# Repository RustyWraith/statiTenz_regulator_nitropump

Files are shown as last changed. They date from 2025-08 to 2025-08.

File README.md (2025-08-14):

# statiTenz_regulator_nitropump

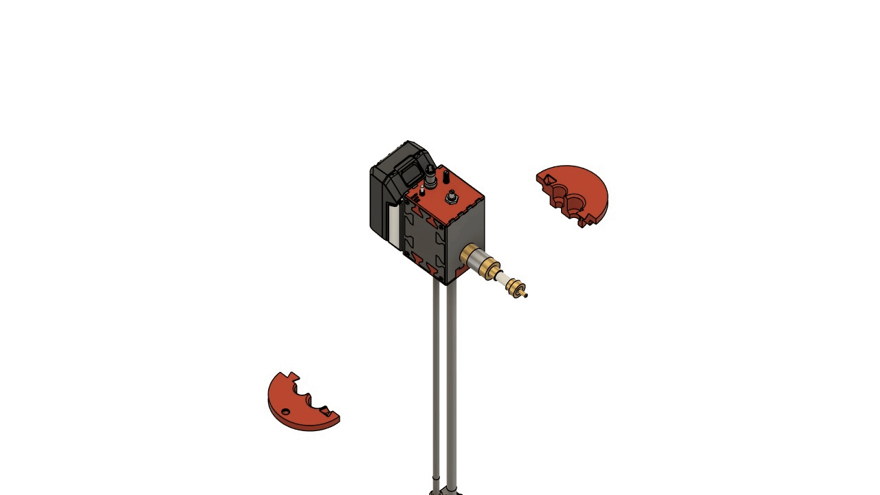
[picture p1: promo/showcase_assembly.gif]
showcase_assembly
  

Designed as part of the [**_statiTenz project_**](https://github.com/topics/statitenz).

## Application

Designed to pump liquid nitrogen from one vessel to another.

## Operating principle

Brushless DC motor actuated impeller pushes liquid nitrogen up the pipe.

## Basic operations

- Switch in **OFF** position
  The device remains powered off.
- Switch in **AUTO** position
  The motor speed is controlled by the PWM pin in the 3-pin connector.
- Switch in **ON** position
  The motor speed is manually controlled using the large knob, while the small knob sets the maximum speed limit.

## Operation tips

📝 Ensure the device is fully cooled before operation.  
📝 The check valve prevents ice formation inside the top part of the device.  
⚠️ **Do not** seal any vessel containing liquid nitrogen.  
⚠️ Exposing the cooled pumping part to the atmosphere will quickly cause ice to form inside the motor. Defrost and dry it at room temperature.  
⚠️ Plastic parts may explode upon cooling or heating. Let them settle at least 10 minutes before handling.  

## Assembly tips

Click on CODE -> Download ZIP to download all project files.  
Assemble the device following the instructions in the CAD_files\drawings folder.  
Refer to the schematics_and_PCBs folder for wiring instructions.  
The bill of materials is available in the CAD_files\buying_BOMs folder.  
Replace the motor's bearings with ceramic ones to ensure proper operation in liquid nitrogen.  
Handle ceramic bearings carefully, as they are fragile. It is recommended to purchase a spare set.  
Use the printed jigs (bearing_removing_jig_1 and bearing_removing_jig_2) to remove the stock bearings.  
PTFE sealing tape works fine.  
PTFE is generally a suitable material for use with liquid nitrogen.  
Print all parts in PETG. While PET performs adequately in liquid nitrogen, it may experience fatigue over time.  

statiTenz_regulator_nitropump_head  

statiTenz_regulator_nitropump_pump  

## Demo

Watch a short demonstraition [here](https://youtu.be/WFPVAQTfw5o) and [here](https://youtu.be/W20JA836Wec).  
Or [here](https://rutube.ru/video/cd4911075f1441f6e3c4c198d58dbadf) and [here](https://rutube.ru/video/834853d1d1c72582e7ad7376b3be9698).  

## Contact the author

Create a new issue.  

## Donate the author

[donate][boosty-link]  

[boosty-link]: https://boosty.to/rustywraith/donate
[boosty-image]: promo/boosty.png

[][cc-by]  
[][cc-by]  

[cc-by]: http://creativecommons.org/licenses/by/4.0/
[cc-by-image]: https://i.creativecommons.org/l/by/4.0/88x31.png
[cc-by-shield]: https://img.shields.io/badge/License-CC%20BY%204.0-lightgrey.svg

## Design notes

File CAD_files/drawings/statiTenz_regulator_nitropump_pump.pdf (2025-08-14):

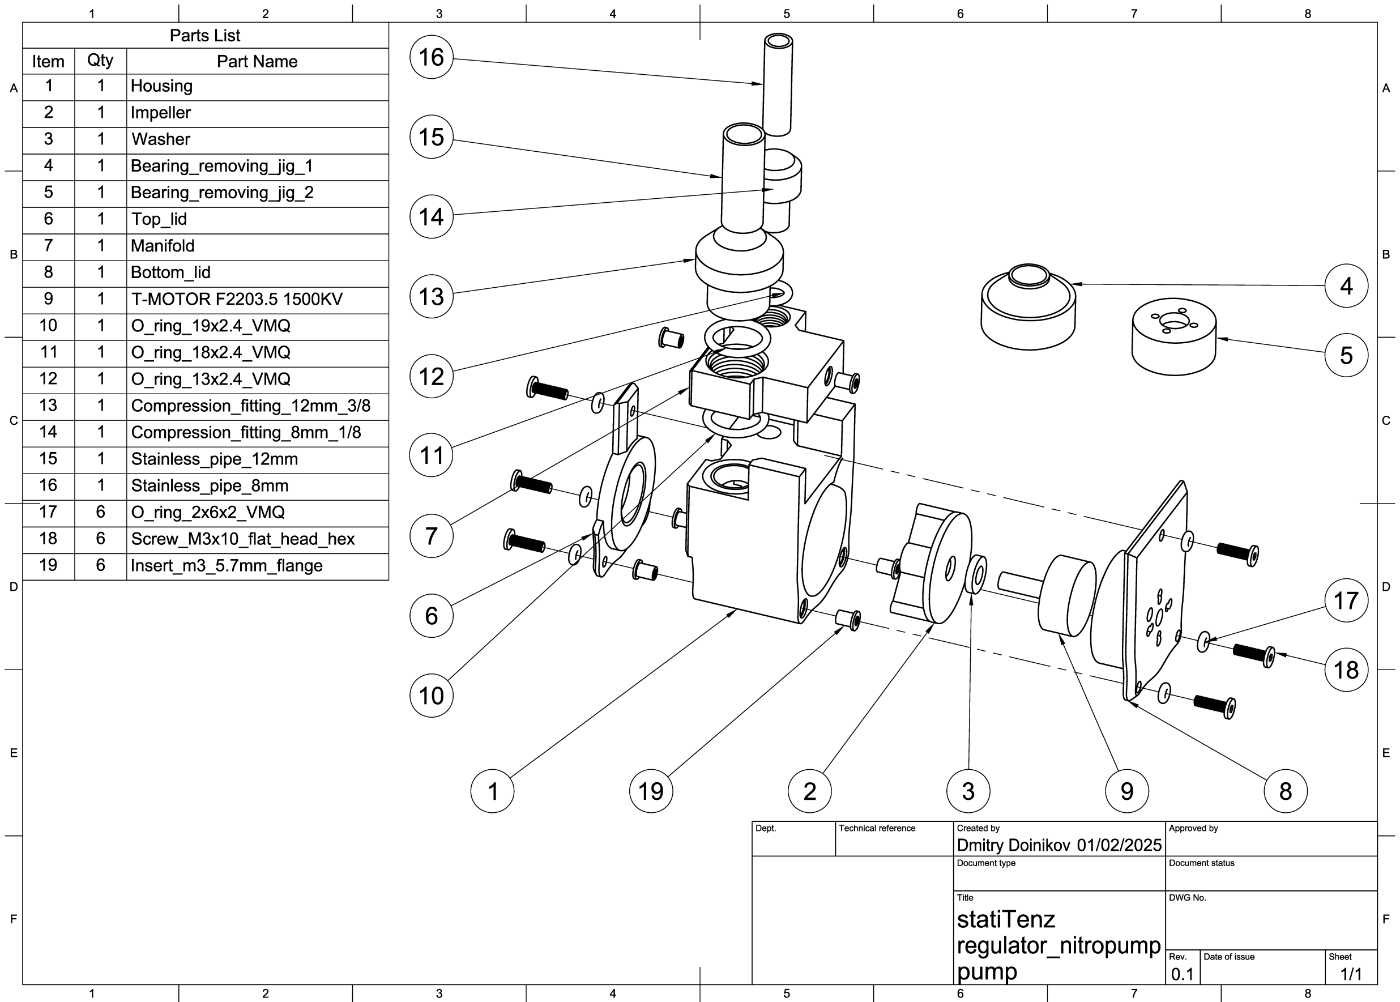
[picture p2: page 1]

1 | 2 | 3 | 4 | 5 | 6 | 7 | 8
Parts List
Item Qty | Part Name
Al | 1 | 1 | Housing | I | --i | I | IA
2 | 1 | Impeller
3 | 1 | Washer
4 | 1 | Bearing_removingjig_ 1
5 | 1 | Bearing_removingjig_ 2
6 | 1 | Top_lid
_----+-. - A | 1B -
7 | 1 | Manifold | I | - Bl I | 8 | 1 | Bottom_lid
9 | 1 | T-MOTOR F2203.5 1500KV
'-..____/
10 | 1 | O_ring_ 19x2.4_VMQ | l~J C o~o
11 | 1 | O_ring_ 18x2.4_VMQ
12 | 1 | O_ring_ 13x2.4_VMQ
Compression_fitting_ 12mm_3/8 1 | IC
13 | 1
c: | ~ | 1 IR -------l '-- ~ i:=::::::n-v---r I Compression_fitting_8mm_ 1/8 | I 14 | 1
15 | 1 | Stainless pipe_ 12mm

# ~(!Jr~~/ -- I

'-...._____/
------ ¹⁶ 1 I Stainless_pipe_8mm | r--.._
------ 17 | 6 | O_ring_2x6x2_ VMQ
18 | 6 | Screw_M3x1 0_flat_head hex
19 | 6 | Insert m3 5. 7mm flange I | - | - | -
D
E | E
Dept. | Technical reference | Created by | Approved by
Dmitry Doinikov 01/02/2025
| | Document type | Document status
Title | DWG No.
F | statiTenz | F
regulator - nitropump I Re, | I"''""'""'~ | Is""" I
umo | 0.1 | 1/1
2 | 3 | 4 | 5 | 6 | 7 | 8

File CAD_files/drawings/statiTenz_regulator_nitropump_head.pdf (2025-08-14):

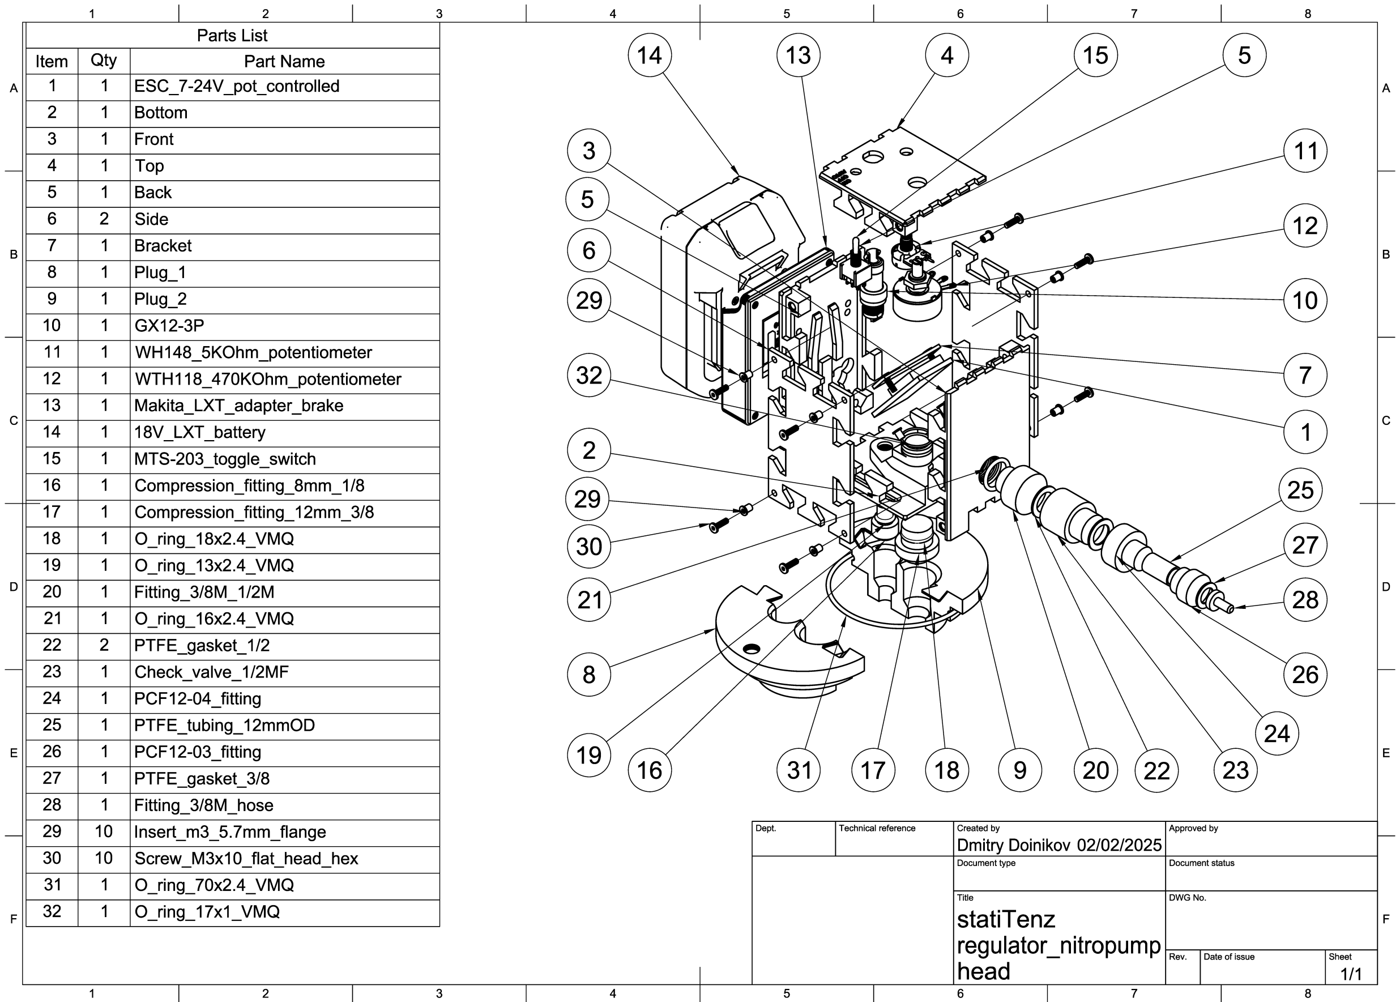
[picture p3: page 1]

2 | 3 | 4 | 5 | 6 | 7 | 8
Parts List
Item | Qty I Part Name
2 | 1 Bottom
3 | 1 I Front
4 | 1 ITop
5 | 1 I Back
6 | 2 ISide
AIL! | 1 | ESC_7-24V_pot_controlled | A
8 11 7 I | 1 I Bracket | I
8 | 1 | Plug_ 1

B

9 I 1 IPlug_2
10 1 I GX12-3P
11 I 1 I WH148_5KOhm_potentiometer
12 I 1 I WTH118_ 470KOhm_potentiometer
13 | 1 | Makita_LXT _adapter_brake
Cl | 14 | 1 | 18V_LXT_battery | C

15 I 1 I MTS-203_toggle_switch
16 | 1 | Compression_fitting_8mm_ 1/8
17 | 1 | Compression_fitting_ 12mm_3/8
18 | 1 | 0 _ring_ 18x2.4_ VMQ
19 | 1 | O_ring_ 13x2.4_VMQ
D | 20 | 1 | Fitting_3/8M_ 1/2M | D
21 | 1 | O_ring_ 16x2.4_VMQ
22 | 2 | PTFE_gasket_ 1 /2
23 | 1 I Check valve 1 /2M F - | -
24 | 1 I PCF12-04_fitting
25 | 1 I PTFE_tubing_ 12mmOD
Ell 26 | 1 I PCF12-03_fitting | E
27 | 1 I PTFE_gasket_3/8
28 | 1 I Fitting_3/8M_hose
29 | 10 I 1nsert_m3_5.7mm_flange
30 | 10 I Screw M3x10 flat head hex - | - | - | -
Dept. | Technical reference | Created by | I Approved by
Dmitry Doinikov 02/02/2025
Document type | I Document status
Title head | I DWG No. 1/1
31 | 1 IO _ring_70x2.4_ VMQ
32 F.
~-~--~-----------------~
1 | 0 _ring_ 17x1 _ VMQ | statiTenz | F
regulator_nitropump I Rev. | IDateofissue | Ishee! | I
2 | 3 | 4 | 5 | 6 | 7 | 8

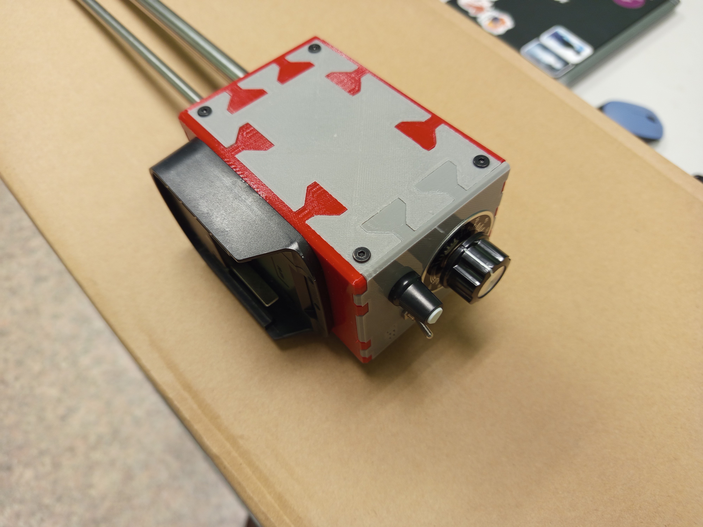
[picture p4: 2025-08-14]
promo/head.jpg

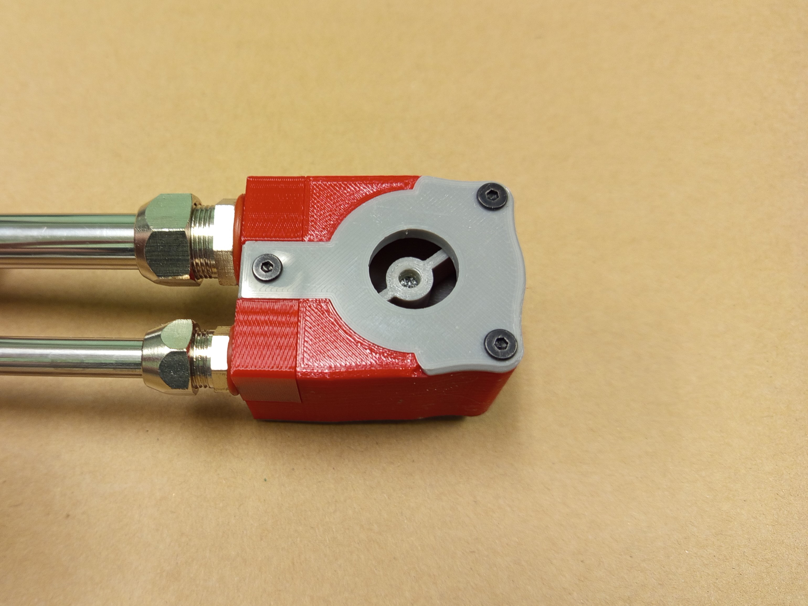
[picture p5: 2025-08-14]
promo/pump.jpg

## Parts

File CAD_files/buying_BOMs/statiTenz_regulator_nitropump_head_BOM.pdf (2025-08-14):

Item | Qty | Part Name | Link | Reference Image | Comment
1 | 1 | ESC_7-24V_pot_controlled | https://sl.aliexpress.ru/p?key=p427GnA
2 | 1 | Bottom
3 | 1 | Front
4 | 1 | Top
5 | 1 | Back
6 | 2 | Side
7 | 1 | Bracket
8 | 1 | Plug_1
9 | 1 | Plug_2
10 | 1 | GX12-3P | https://sl.aliexpress.ru/p?key=bd27G5X

Item | Qty | Part Name | Link | Reference Image | Comment
11 | 1 | WH148_5KOhm_potentiometer | https://sl.aliexpress.ru/p?key=3p27GzG
12 | 1 | WTH118_470KOhm_potentiometer | https://sl.aliexpress.ru/p?key=On27GY1
13 | 1 | Makita_LXT_adapter_brake | https://sl.aliexpress.ru/p?key=ev27Gs7
14 | 1 | 18V_LXT_battery
15 | 1 | MTS-203_toggle_switch | https://sl.aliexpress.ru/p?key=ko27GoM

Item | Qty | Part Name | Link | Reference Image | Comment
16 | 1 | Compression_fitting_8mm_1/8
17 | 1 | Compression_fitting_12mm_3/8
18 | 1 | O_ring_18x2.4_VMQ
19 | 1 | O_ring_13x2.4_VMQ
20 | 1 | Fitting_3/8M_1/2M
21 | 1 | O_ring_16x2.4_VMQ
22 | 2 | PTFE_gasket_1/2
23 | 1 | Check_valve_1/2MF | https://sl.aliexpress.ru/p?key=SR27G2m
24 | 1 | PCF12-04_fitting
25 | 1 | PTFE_tubing_12mmOD (1 meter)
26 | 1 | PCF12-03_fitting
27 | 1 | PTFE_gasket_3/8
28 | 1 | Fitting_3/8M_hose
29 | 10 | Insert_m3_5.7mm_flange
30 | 10 | Screw_M3x10_flat_head_hex
31 | 1 | O_ring_70x2.4_VMQ
32 | 1 | O_ring_17x1_VMQ

33 | 1 | Wire ПВС 3х0.5 мм2 or western analogue

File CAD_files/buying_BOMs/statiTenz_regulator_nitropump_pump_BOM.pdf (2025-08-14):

Item | Qty | Part Name | Link | Reference Image | Comment
1 | 1 | Housing
2 | 1 | Impeller
3 | 1 | Washer
4 | 1 | Bearing_removingjig_1
5 | 1 | Bearing_removingjig_2
6 | 1 | Top_lid
7 | 1 | Manifold
8 | 1 | Bottom_lid
9 | 1 | T-MOTOR_F2203.5_1500KV | https://sl.aliexpress.ru/p?key=xElLGM4
10 | 1 | O_ring_19x2.4_VMQ | https://sl.aliexpress.ru/p?key=11lLGxF
11 | 1 | O_ring_18x2.4_VMQ | https://sl.aliexpress.ru/p?key=11lLGxF
12 | 1 | O_ring_13x2.4_VMQ | https://sl.aliexpress.ru/p?key=11lLGxF

Item | Qty | Part Name | Link | Reference Image | Comment
13 | 1 | Compression_fitting_12mm_3/8
14 | 1 | Compression_fitting_8mm_1/8
15 | 1 | Stainless_pipe_12mm
16 | 1 | Stainless_pipe_8mm
17 | 6 | O_ring_2x6x2_VMQ | https://sl.aliexpress.ru/p?key=11lLGxF
18 | 6 | Screw_M3x10_flat_head_hex
19 | 6 | Insert_m3_5.7mm_flange

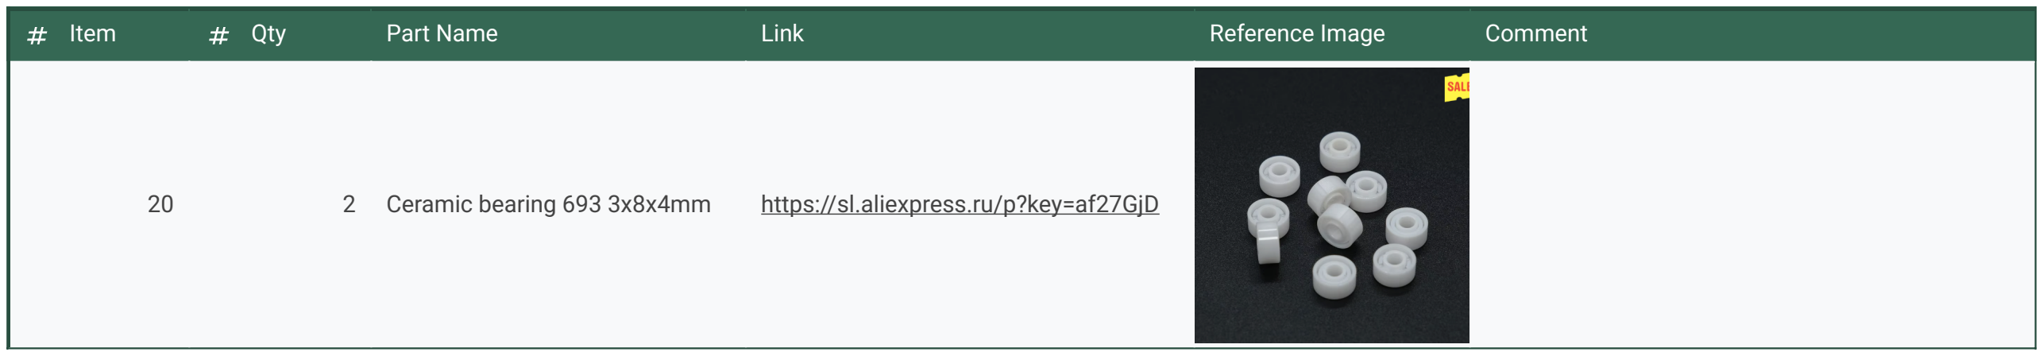
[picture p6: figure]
Item; Qty; Part Name; Link; Reference Image; Comment; Ceramic bearing 693 3x8x4mm; https://sl.aliexpress.ru/p?key=af27GjD

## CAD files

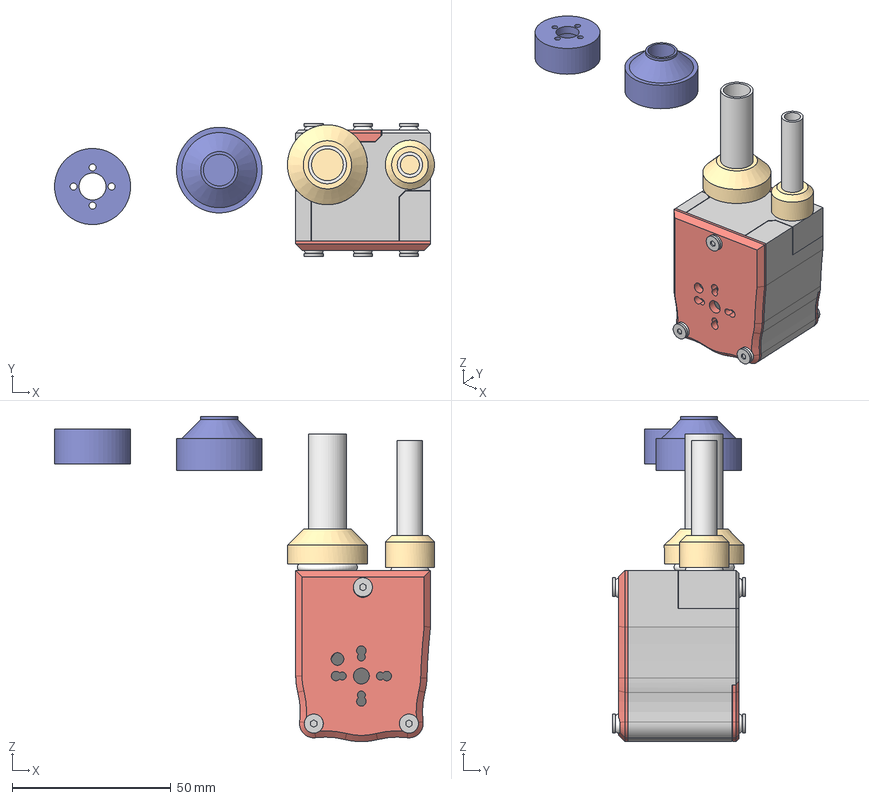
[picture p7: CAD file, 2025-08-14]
CAD_files/projects/statiTenz_regulator_nitropump_pump.step
119.8 x 41.9 x 102.5 mm
housing
bottom_lid
top_lid
manifold
impeller
washer
bearing_removing_jig_1
bearing_removing_jig_2
T-MOTOR F2203.5 1500KV
o_ring_19x2.4_VMQ
o_ring_18x2.4_VMQ
o_ring_13x2.4_VMQ
compression_fitting_12mm_3/8
compression_fitting_8mm_1/8
stainless_pipe_12mm
stainless_pipe_8mm
o_ring_2x6x2_VMQ x 6
screw_M3x10_flat_head_hex x 6
insert_m3_5.7mm_flange x 6

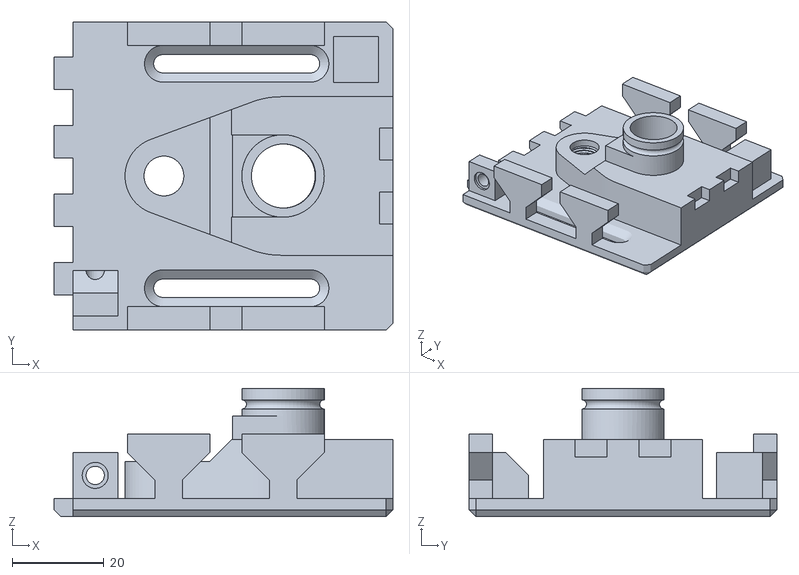
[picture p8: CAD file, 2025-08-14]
CAD_files/STLs/STL_statiTenz_regulator_nitropump_head v77_bottom_1_Body1.stl
74.0 x 67.2 x 28.0

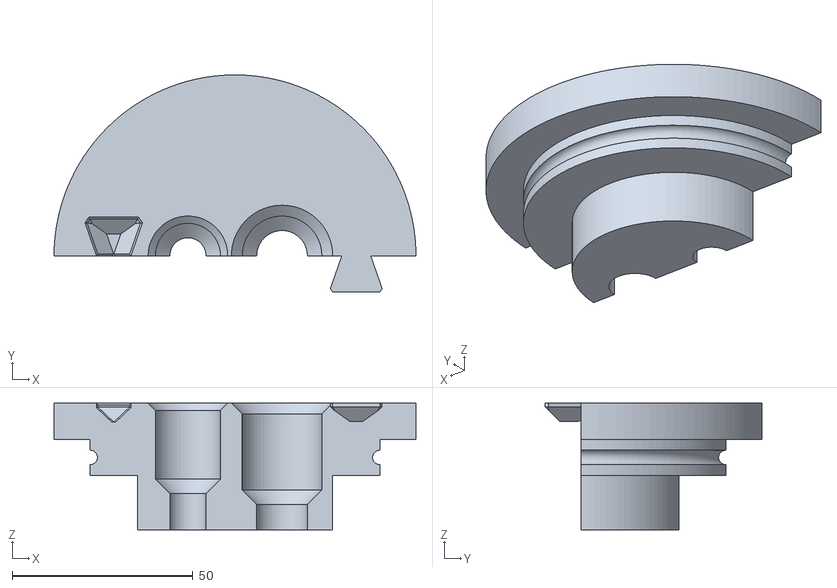
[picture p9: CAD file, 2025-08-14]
CAD_files/STLs/STL_statiTenz_regulator_nitropump_head v77_plug_2_1_Body1.stl
100.0 x 60.0 x 35.0

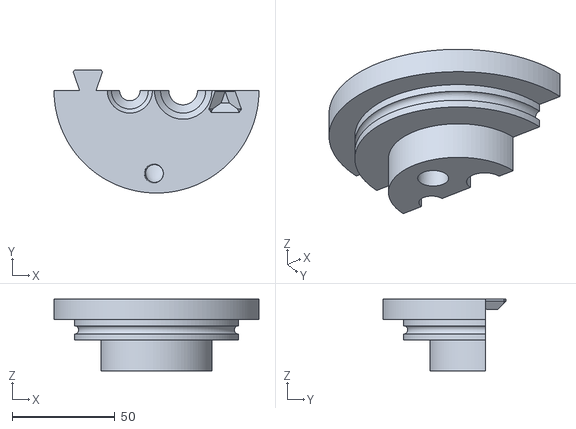
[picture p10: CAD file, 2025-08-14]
CAD_files/STLs/STL_statiTenz_regulator_nitropump_head v77_plug_1_1_Body1.stl
100.0 x 60.0 x 35.0

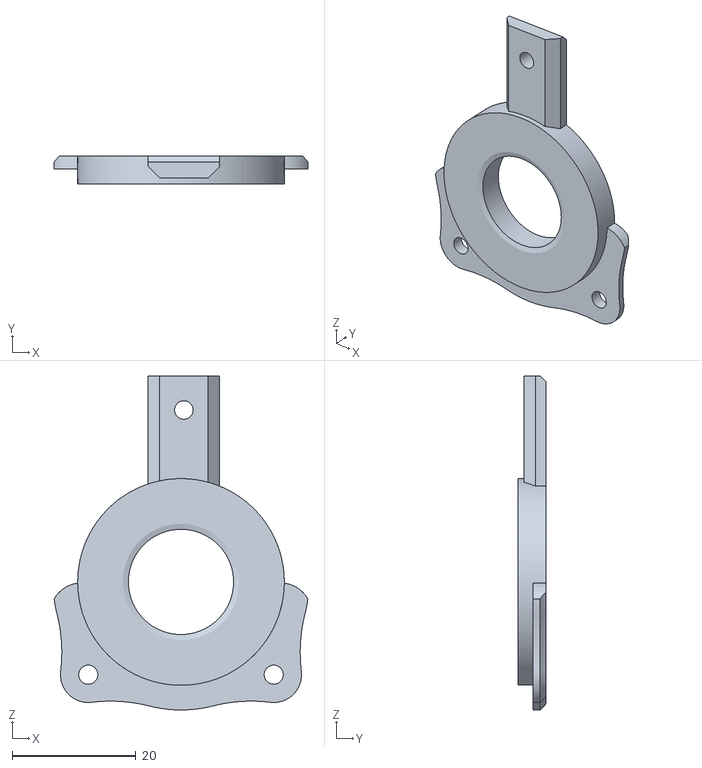
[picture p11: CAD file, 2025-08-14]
CAD_files/STLs/STL_statiTenz_regulator_nitropump_pump v42_top_lid_1_Body1.stl
41.0 x 4.60 x 54.0

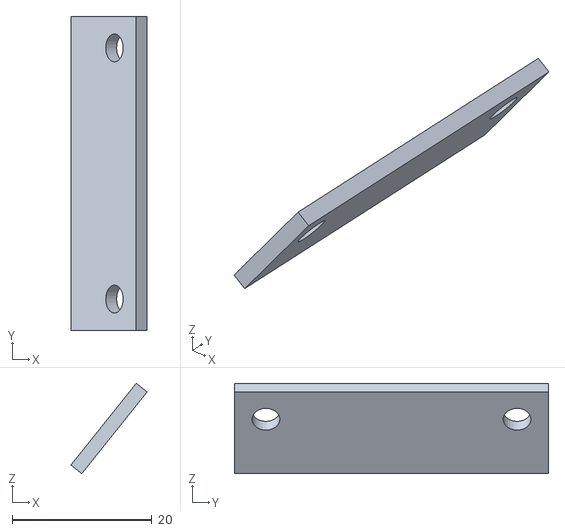
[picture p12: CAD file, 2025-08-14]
CAD_files/STLs/STL_statiTenz_regulator_nitropump_head v77_bracket_1_Body1.stl
10.9 x 45.0 x 13.0

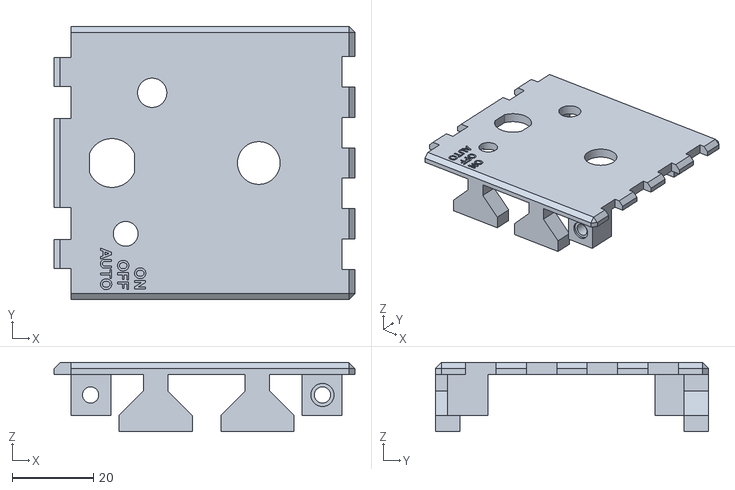
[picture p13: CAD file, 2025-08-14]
CAD_files/STLs/STL_statiTenz_regulator_nitropump_head v77_top_1_Body1.stl
74.0 x 67.2 x 17.0

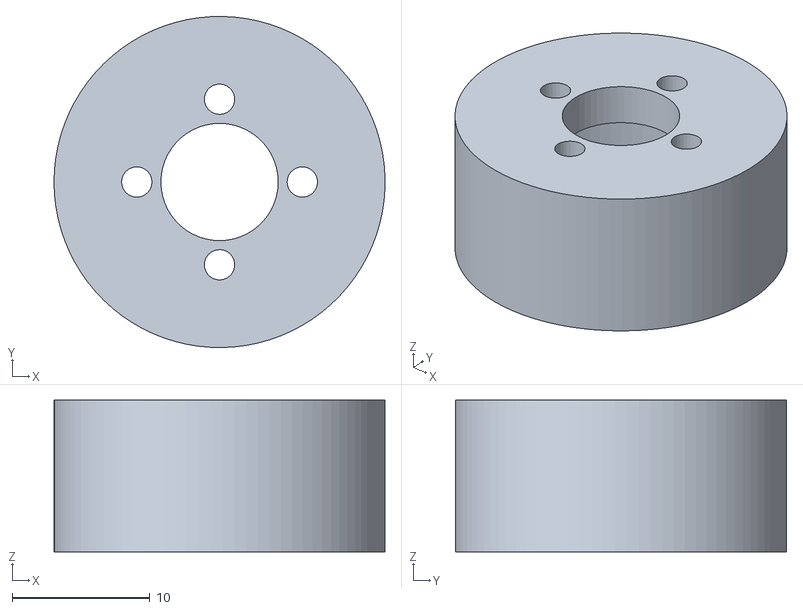
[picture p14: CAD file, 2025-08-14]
CAD_files/STLs/STL_statiTenz_regulator_nitropump_pump v42_bearing_removing_jig_2_1_Body1.stl
24.0 x 24.0 x 11.0

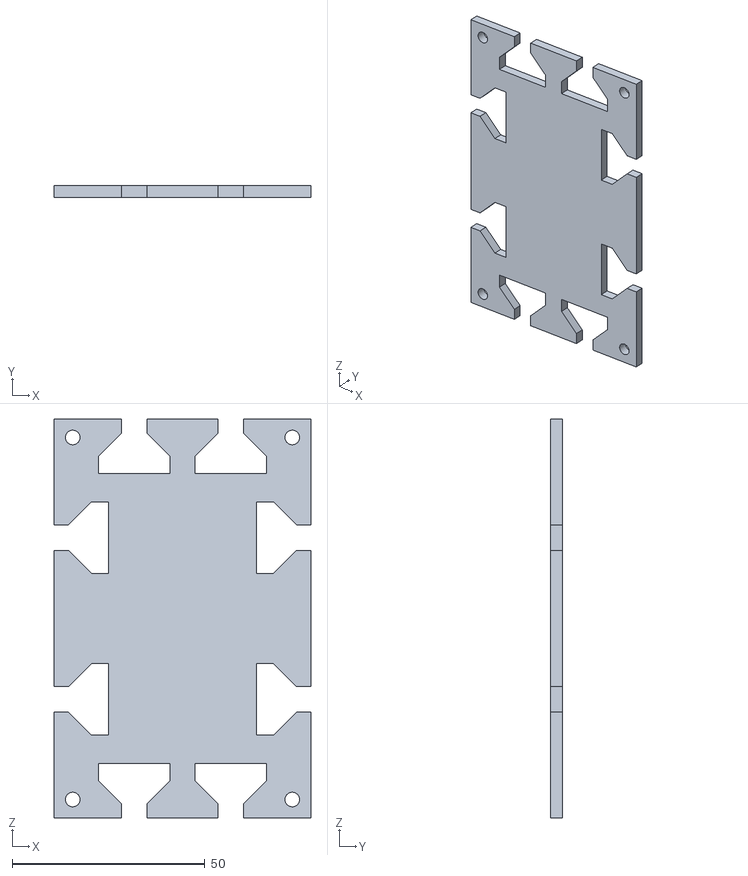
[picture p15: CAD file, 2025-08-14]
CAD_files/STLs/STL_statiTenz_regulator_nitropump_head v77_side_1_Body1.stl
66.6 x 3.00 x 103.6

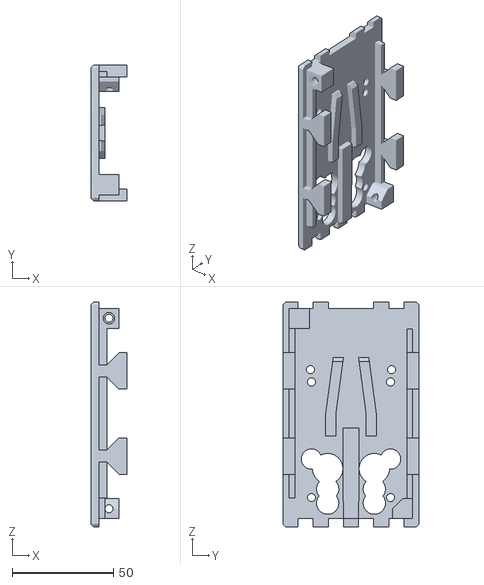
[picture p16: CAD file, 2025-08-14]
CAD_files/STLs/STL_statiTenz_regulator_nitropump_head v77_back_1_Body1.stl
18.0 x 67.2 x 111.0

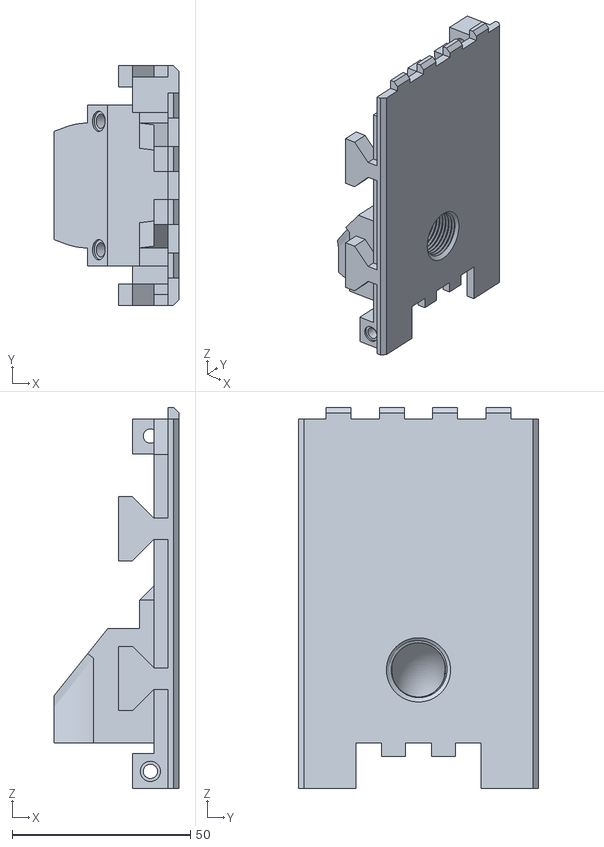
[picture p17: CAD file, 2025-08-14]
CAD_files/STLs/STL_statiTenz_regulator_nitropump_head v77_front_1_Body2.stl
35.0 x 67.2 x 106.8

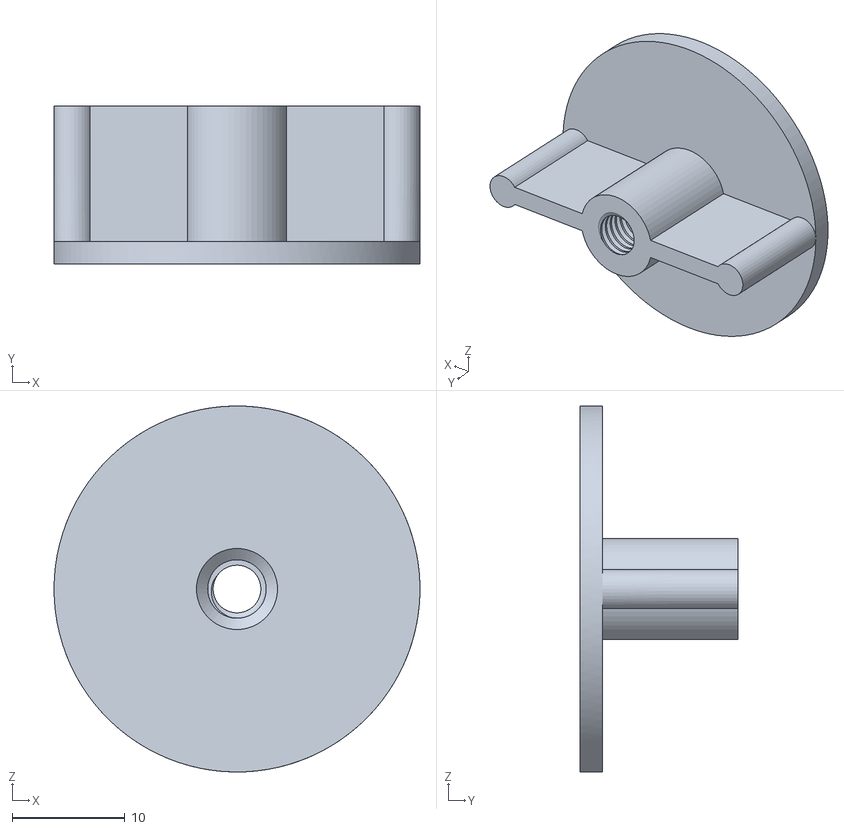
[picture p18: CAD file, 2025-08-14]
CAD_files/STLs/STL_statiTenz_regulator_nitropump_pump v42_impeller_1_Body1.stl
32.5 x 14.0 x 32.5

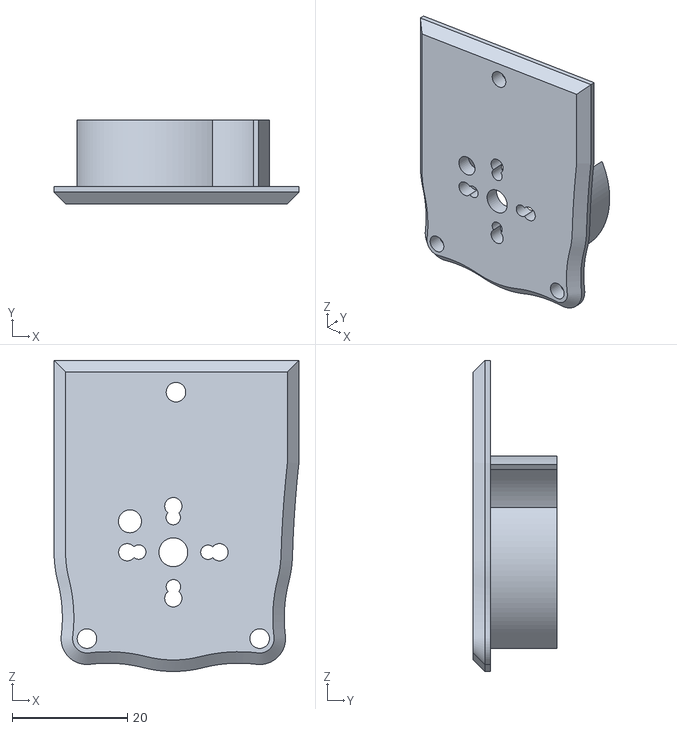
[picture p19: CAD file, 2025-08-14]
CAD_files/STLs/STL_statiTenz_regulator_nitropump_pump v42_bottom_lid_1_Body1.stl
42.5 x 14.5 x 54.0

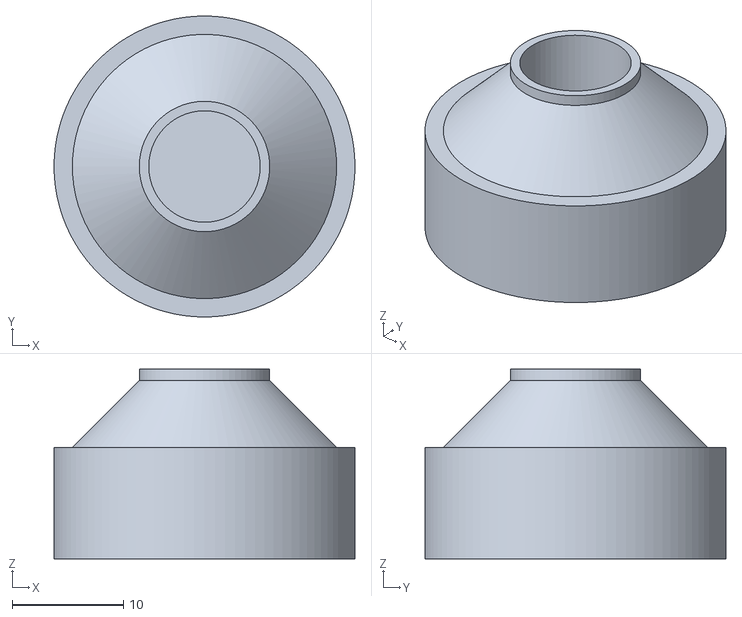
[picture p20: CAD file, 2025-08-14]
CAD_files/STLs/STL_statiTenz_regulator_nitropump_pump v42_bearing_removing_jig_1_1_Body1.stl
27.0 x 27.0 x 17.0

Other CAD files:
CAD_files/STLs/STL_statiTenz_regulator_nitropump_pump v42_manifold_1_Body1.stl
CAD_files/STLs/STL_statiTenz_regulator_nitropump_pump v42_housing_1_Body1.stl
CAD_files/STLs/STL_statiTenz_regulator_nitropump_pump v42_washer_1_Body1.stl
CAD_files/projects/statiTenz_regulator_nitropump_head.f3d
CAD_files/projects/statiTenz_regulator_nitropump_pump.f3d

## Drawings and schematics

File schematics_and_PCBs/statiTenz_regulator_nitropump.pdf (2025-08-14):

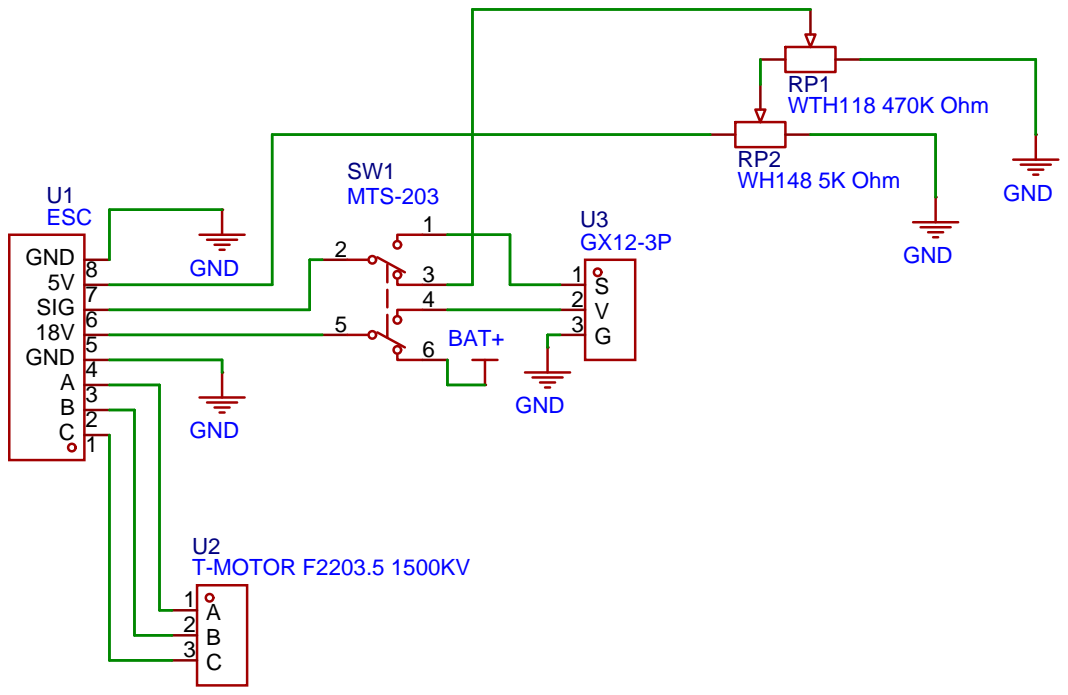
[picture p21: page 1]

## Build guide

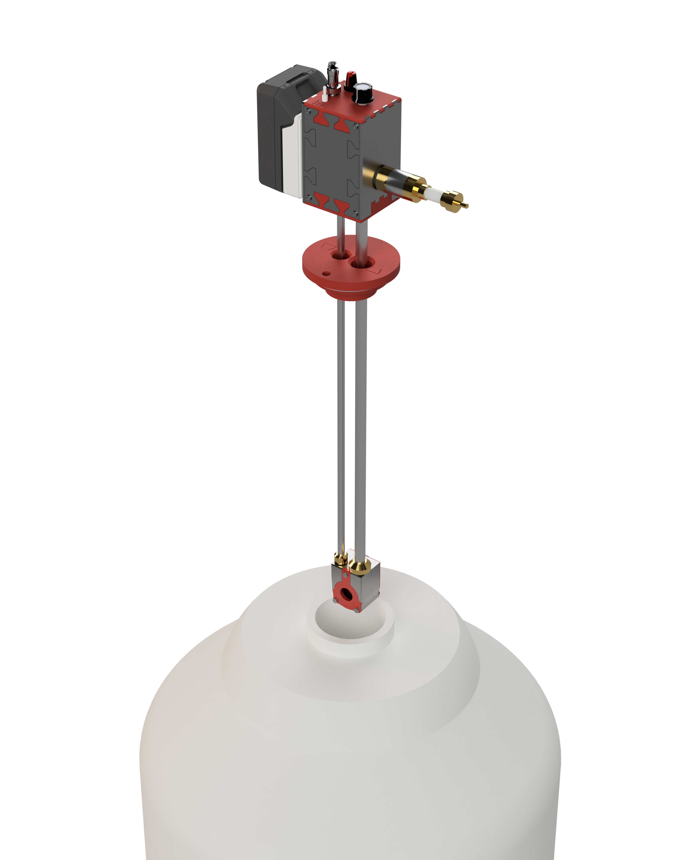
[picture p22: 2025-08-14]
promo/showcase_assembly.PNG

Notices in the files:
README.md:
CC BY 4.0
